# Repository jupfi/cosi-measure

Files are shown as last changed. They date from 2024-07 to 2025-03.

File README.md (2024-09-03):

# COSI Measure

COSI Measure

<!-- TOC -->

- [COSI Measure](#cosi-measure)
  - [Description](#description)
  - [System specifications](#system-specifications)
  - [Versions and Branches](#versions-and-branches)
  - [Contacts](#contacts)
    - [Known builds](#known-builds)
  - [Contributors alphabetical order](#contributors-alphabetical-order)
  - [Publications](#publications)
  - [Acknowledgments](#acknowledgments)
  - [License and Liability](#license-and-liability)

<!-- /TOC -->
## Description

COSI Measure is an open source multipurpose 3-axis robot operating in a large volume, that can be equipped with e.g. field mapping probes for static or dynamic field measurements (electromagnetic, temperature etc.). Submillimeter fidelity and reproducibility/backlash performance were evaluated experimentally. It can be potentially upgraded to be used as a CNC, for 3D printing or other applications, that require reproducible submillimeter movements.

## System specifications

- Dimension: (80x90x105)cm³
- Working volume: (53x53x64)cm³
- Precision: positioning error <1mm
- Max load: ~20kg
- Applied force: 896N (91kg)
- Standalone system
- Inductive limit switches
- Emergency Stop
- Open Source Software GUI (Python)
- Estimated material costs: ~2000€

More photos and videos can be found on opensourceimaging.org: <https://www.opensourceimaging.org/project/cosi-measure/>

## Versions and Branches

You're currently viewing the `main` branch, showing ongoing development on `v2.0.*` of the COSI Measure system.\
New versions are developed in dedicated feature branches and then merged here.

The latest stable release is [v2.0](https://github.com/opensourceimaging/cosi-measure/releases/tag/v2.0).

For older, please check out the [releases overview](https://github.com/opensourceimaging/cosi-measure/releases/).

The changes between versions are summarized in the respective release notes and documented in the [CHANGELOG](CHANGELOG.md) document.

## Contacts

General contact:
Name | Email | Institution | COSI Measure Applications
-----|-----|-----|-----|
Lukas Winter | <lukas.winter@ptb.de> | Physikalisch-Technische Bundesanstalt (PTB), Berlin, Germany | Magnetic field mapping of MR magnets, implant safety measurements, RF field mapping of RF coils using time-domain H- and E-field sensors, Measurements within an MR scanner, 3D printing

COSI Measure Builds

### (Known) builds

Name | Email | Institution | COSI Measure Applications
-----|-----|-----|-----|
Haopeng Han | <haopeng.han@mdc-berlin.de> | Max-Delbrück Center for Molecular Medicine, Berlin, Germany | Temperature and RF field mapping of RF coils
Tom O'Reilly | <t.o_reilly@lumc.nl> | Leiden University Medical Center (LUMC), Leiden, Netherlands | Magnetic field mapping of low field MR magnets
Benjamin Menküc | <benjamin.menkuec@fh-dortmund.de> | University of Applied Sciences, Dortmund, Germany | Magnetic field mapping of low field MR magnets
Mark Bason | <M.Bason@sussex.ac.uk> | Quantum Systems and Devices, University of Sussex, Falmer, England | Magnetic field measurements
Wolfgang Kilian | <Wolfgang.Kilian@ptb.de> | Physikalisch-Technische Bundesanstalt (PTB), Berlin, Germany | 3D printing of phantoms

## Contributors (alphabetical order)

Nils Allek, Mark Bason, Jan Gregor Frintz, Haopeng Han, Amjad Kasabashy, Wolfgang Kilian, Ilia Kulikov, Benjamin Menküc, Tobias Mohr, Reiner Montag, Tom O'Reilly, David Shiers, Berk Silemek, Karl Stupic, Lukas Winter

## Publications

If you find this useful in your work, please cite:
[H. Han, R. Moritz, E. Oberacker, H. Waiczies, T. Niendorf and L. Winter, "Open Source 3D Multipurpose Measurement System with Submillimetre Fidelity and First Application in Magnetic Resonance", Scientific Reports, 7:13452, 2017](https://nature.com/articles/s41598-017-13824-z)

## Acknowledgments

This work is supported by the Open Source Imaging Initiative (OSI²), <https://www.opensourceimaging.org/project/cosi-measure/>

The project (21NRM05) has received funding from the European Partnership on Metrology, co-financed by the European Union's Horizon Europe Research and Innovation Programme and by the Participating States.

## License and Liability

The content in this repository is licensed under the CERN Open Hardware Licence Version 2 - Weakly Reciprocal, please see [LICENSE](LICENSE) for details and also check the [DISCLAIMER](DISCLAIMER.pdf)

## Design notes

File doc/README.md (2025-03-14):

# COSI Measure Assembly

To build your own COSI measure, you will need to complete the following steps:

- Finish the [Mechanical Assembly](mechanical_assembly.md). This contains the steps to assemble the mechanical components of the COSI measure.
- Finish the [Enclosure Assembly](enclosure_assembly.md). This contains the steps for wiring the electronics and assembling the enclosure. This has some subitems that need to be completed in order to finish the enclosure assembly.
  - Build the [Driver Breakoutboard](rumba32/driver_breakoutboard_assembly.md). This contains the steps to assemble the driver breakoutboard.
  - Build the [Endstop Levelshifter](rumba32/endstop_levelshifter_assembly.md). This contains the steps to assemble the endstop levelshifter.
- Finish the wiring of the [Sensors and Actuators](wiring_sensor_actuators.md). This contains the steps for wiring the sensors and actuators to the electronics cabinet.

You can then commission the COSI measure by following the steps in the [Commissioning](comissioning.md) section.

Once you have completed these steps, you will have a fully assembled COSI measure. You can then follow the steps in the [Software Setup](software_setup.md) to configure the software for your COSI measure.

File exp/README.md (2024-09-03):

# Exports

This folder contains all exports that are relevant for the COSI Measure (3D printable STLS, Gerber files, etc.).

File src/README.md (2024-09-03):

# System

Here you can find all necessary files to reproduce the COSI Measure setup.

Please read the [assembly documentation](../doc/README.md) first, in particular you will find some known issues or useful ideas in the comments section, which will help you reproducing the design.

## Mechanical

The mechanical design contains the BoM and technical drawings of the mechanical parts.

## Enclosure

The enclosure design contains the BoM and design files of electronic cabinet components.

## Motors and Sensors

Contains designs for the motors and sensors.

## Software

The software design contains the configuration files for the Klipper firmware.

## Accessories

Contains designs for accessories like the field mapping probe.

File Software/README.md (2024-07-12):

# Software Getting Started

<!-- TOC -->

- [Software Getting Started](#software-getting-started)
    - [Installation](#installation)
        - [Download and Install Klipper](#download-and-install-klipper)
        - [Setting things up!](#setting-things-up)
        - [Config File](#config-file)
        - [Going into Bootloader Mode](#going-into-bootloader-mode)
        - [Flashing MCU and getting new Serial Port](#flashing-mcu-and-getting-new-serial-port)
    - [GUI](#gui)
    - [Commandline Interface](#commandline-interface)

<!-- /TOC -->

COSY Measure is using the open source 3D-printer firmware [klipper](https://www.klipper3d.org/). This document leads you through the installation. It´s assumed you have already installed [Raspberry-Pi-OS](https://www.raspberrypi.com/software/). We recommend the latest 64-bit Desktop version.

## Installation 

This Quick-Start-Guide is a short summary of https://www.klipper3d.org/Installation.html with some modifications for Rumba32 boards.

### 1. Download and Install Klipper

     git clone https://github.com/Klipper3d/klipper
     ./klipper/scripts/install-octopi.sh

Go to [backend/flash_mcu.sh](backend/flash_mcu.sh) and change the path in line 19 to the path of the repository above. For me line 19 is 

     19:  cd /home/cosi/klipper

### 2.1 Setting things up!

     cd klipper
     make menuconfig 

Opens a menu. Set
- Enable extra low-level configuration options
- Micro-controller Architecture (STMicroelectronics STM32)
- Processor model (STM32F446)
- Bootloader offset (32KiB bootloader)
- Clock Reference (12 MHz crystal)
- Communication interface (USB (on PA11/PA12))
- USB ids (doesnt matter. But choose something)
- no GPIO pins to set at startup ()

### 2.2 Config File

Get or write a ```printer.cfg```-file, here is mine: [backend/printer.cfg](backend/printer.cfg)

Save it as a file named "printer.cfg" in the home directory of the pi user (i.e. ```/home/cosi/printer.cfg```).

This file contains all machine configurations. Further reading: https://www.klipper3d.org/Installation.html#obtain-a-klipper-configuration-file

### 3. Going into Bootloader Mode

If not already done, install ```pigpio```for controlling the GPIO pins via the comand line: 

     sudo apt-get install pigpio
     sudo systemctl enable pigpiod
     sudo systemctl start pigpiod

The shell script ```backend/flash_mcu.sh``` will set the Rumba board into bootloader mode and eventually will try to flash the MCU. Execute 

     ./backend/flash_mcu.sh

to set the board into bootloader mode. Because it doesn´t know yet the usb-id of the microcontroller it will fail to flash - ignore that for now. Search the Device ID by executing 

     lsusb

This will show up something like

     Bus 002 Device 001: ID 1d6b:0003 Linux Foundation 3.0 root hub
     Bus 001 Device 031: ID 0483:df11 STMicroelectronics STM Device in DFU Mode
     Bus 001 Device 002: ID 2109:3431 VIA Labs, Inc. Hub

So in my installatiom ```0483:df11``` is the ID of the STM-chip of Rumba32. Change line 20 in ```backend/flash_mcu.sh``` to your device ID and save the file.

### 4. Flashing MCU and getting new Serial Port

Execute ```backend/flash_mcu.sh``` again. Now it shall flash the MCU. This will eventually look something like

     Downloading to address = 0x08008000, size = 29236
     Download	[=========================] 100%        29236 bytes
     Download done.
     File downloaded successfully
     Transitioning to dfuMANIFEST state
     dfu-util: can't detach
     Resetting USB to switch back to runtime mode
     cosi@raspberrypi:~/klipper $ 

Then search for serial ports by executing 

     ls /dev/serial/by-id/*

this will return something similar to 

     /dev/serial/by-id/usb-Klipper_stm32f446xx_280058000951363131343032-if00

Copy and paste it in ```/home/cosi/printer.cfg``` to your MCU serial definition:

     [mcu]
     serial: /dev/serial/by-id/usb-Klipper_stm32f446xx_280058000951363131343032-if00

Congratulations, now you´re done. Get a coffee. Enjoy.

## GUI

A GUI was developed in Python for COSI measure. You can install all required packages (ideally in a virtual environment) by running:

```bash
pip install -r requirements.txt
```

To start the GUI, run:

```bash
python main.py
```

## Commandline Interface

Start the klipper service with executing

     sudo service klipper start

Klipper can be controlled via the following virtual serial port:

     /tmp/printer

Use 250000 Baud for communication. You can send G-code to this serial port and receive status information of the machine, refer to https://www.klipper3d.org/G-Codes.html. 

There are some custom g-code macros for disabling and enabling the drives without letting klipper loose it´s homing, for details see [printer.cfg](backend/printer.cfg) and [driver breakoutboard](../electronic-cabinet/Rumba32/Driver_BreakoutBoard/README.md). Use this commands only at standstill and never run a movement with disabled drives as this would eventually lead to false positioning.

Stop the klipper service by executing

     sudo service klipper stop

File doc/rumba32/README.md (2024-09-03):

# Rumba32

The [Rumba32](https://github.com/Aus3D/RUMBA32) is a 3D-printer mainboard with a microcontroller which is controlling the stepper motors, endstops etc.

- It is not compatible with industrial 12 V or 24 V limit switches so a levelshifter is needed, see [here](endstop_levelshifter_assembly.md).
- It is not designed for external motor drivers with extended safe-torque-off (emergency stop) functionality, so breakoutboards instead of the motor drivers are needed, see [here](driver_breakoutboard_assembly.md).
- The external motor drivers need 5 V signals, thus a little work on the Rumba32 PCB is needed, see [here](driver_breakoutboard_assembly.md#stepper_driver_logic-jumper)
- [Klipper](https://github.com/Klipper3d/klipper) requires a temperature signal from the nozzle and the heated bed. COSI Measure usually does not have this, so please plug two 100 k resistors to the PT100 inputs.

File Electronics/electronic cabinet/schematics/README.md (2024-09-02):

# Schematics and Terminal Plans

<!-- TOC -->

- [Schematics](#schematics)
  - [Power Distribution](#power-distribution)
  - [EmergencyStop](#emergencystop)
    - [Required Specs](#required-specs)
  - [Rumba32 and Motors](#rumba32-and-motors)
    - [NEMA color codes](#nema-color-codes)
  - [RaspberryPi](#raspberrypi)
- [Terminal Plans](#terminal-plans)
  - [X0](#x0)
  - [X1](#x1)
  - [X2](#x2)
  - [X3](#x3)
  - [X4](#x4)
  - [X5](#x5)
  - [X6](#x6)
  - [X7](#x7)
  - [X8](#x8)

<!-- /TOC -->

## Schematics

### Power Distribution

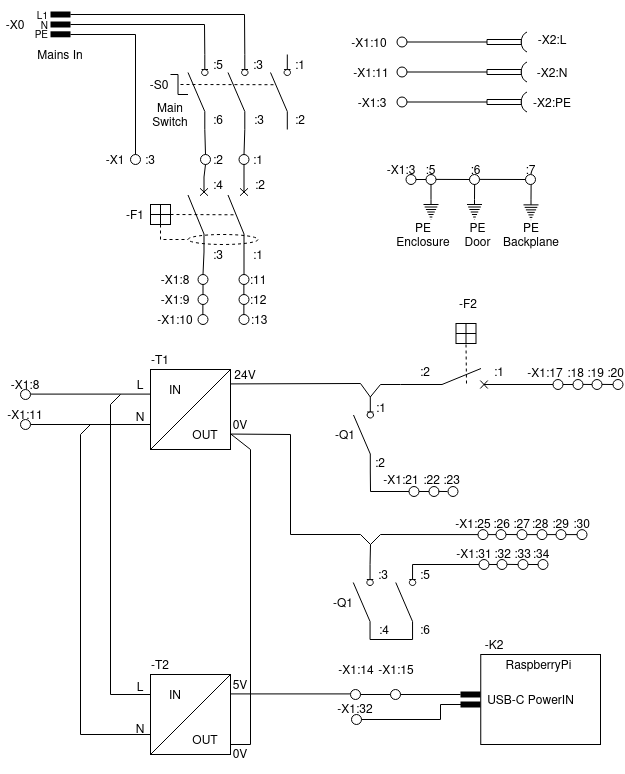
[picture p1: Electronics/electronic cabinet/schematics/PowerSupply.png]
Power Supply Schematic


The contactor $-Q1$ disconnects the motor drivers from the power supply in case of safe-torque-off (aka emergency stop). Schneider Electric has defined this way of wiring in an [application note](https://ckm-content.se.com/ckmContent/sfc/servlet.shepherd/document/download/0691H000008h5vrQAA).

$-F1$ is an overcurrent protection with RCD. Depending to the electric installation of your lab and applicable regional laws it might be optional.

$-F2$ is an overcurrent protection.

### EmergencyStop

It is advisable (and most likely legal obligatory) having a safe-torque-off functionality according to EN-IS0 60204-1 so that the machine can be stopped in case of an emergency. <br>

### Required Specs

- Since the Rumba32 has no failsafe features (SIL-2 or above), the safe-torque-off must be implemented in dedicated hardware.
- To prevent unintended re-start of the drives, a dedicated safety-relais is used (-K1, _XPSUDN13AP_, Schneider Electric). The safety-relais is used with application function '6'. Start function is '1'.
- since there are no stepper motor drivers available with suitable enable inputs (high-active and approved to EN-ISO 60204-1), their enable-inputs can not be used for a safe-torque-off function. So a suitable contactor (DC-3 operation for $20 \ A$ at $24 \ V_{DC}$) must be used to cut-off the power supply to the motor drivers in case of an emergency. This contactor must be selected carefully and wired according to the manufacturers guidelines to ensure safe operation.
- with some bad luck a cheap stepper motor driver can get killed by disrupting the power supply during operation due to the back-EMF of the motor. So a motor driver has to be disabled by the enable pin before interrupting the power supply connection. A 5V signal is sent to the enbable pin of the breakout board if the safety relays turns of. This signal is assumed to be faster than the motors turning off because Q1 is a mechanical relay (switching off the machine by -S0 is always safe: the big $24 \ V$ power supply will slowly turn off the power and eventually take up most of the energy that might return from the drives.)
- The enable input of the motor drivers is used for disabling the drives while performing a field-measurement at an already reached location. This functionality is non safety-relevant, thus it can be implemented the easy way.

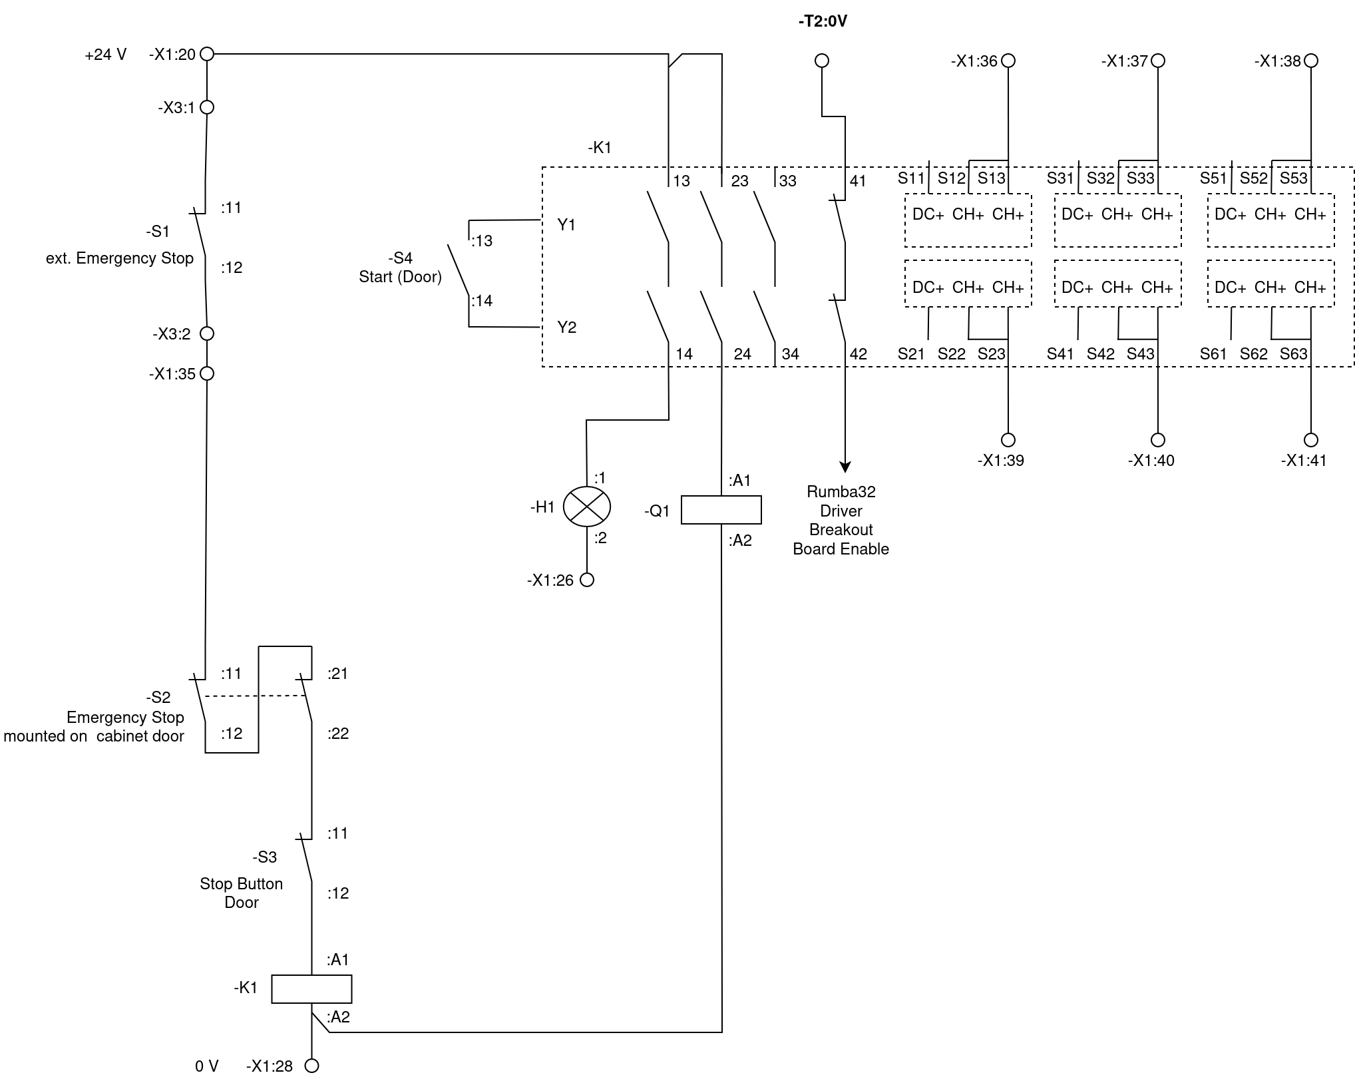
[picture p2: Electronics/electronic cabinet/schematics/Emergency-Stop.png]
Emergency Stop


## Rumba32 and Motors

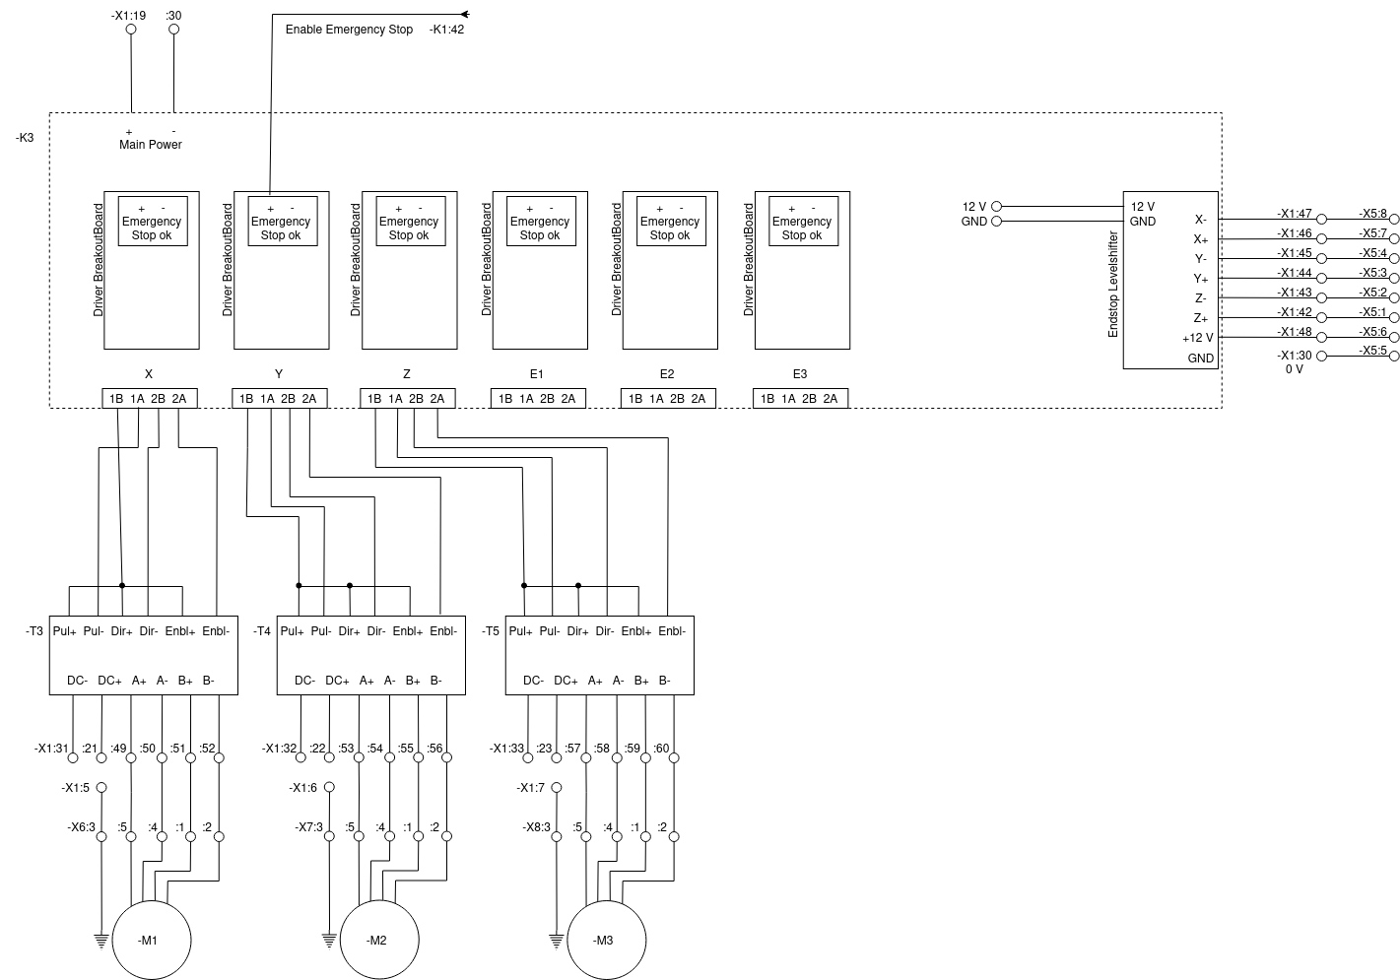
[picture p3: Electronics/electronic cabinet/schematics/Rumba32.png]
Rumba32


The [Rumba32](https://github.com/Aus3D/RUMBA32) is a 3D printer board. It is used for time-critical stuff e.g. generate the step and direction pulses for the stepper motor drivers. <br>
The Driver Breakoutboards are little custom PCBs plugged into the Rumba32, [here](../Rumba32/Driver_BreakoutBoard/README.md) is further documentation about them.

### NEMA color codes

NEMA stepper motors usually have short color-coded wires. Unfortunately, there are multiple colorschemes used. However, some widely used color schemes are in the table below:

| Function  | scheme a  | scheme b  | cable core no | motor connector contact   |
| ----      | ----      | ----      | ----          | ---                       |
| A+        | black     |red        | 1             | :5                        |
| A-        | green     |green      | 2             | :4                        |
| B+        | red       |blue       | 3             | :1                        |
| B-        | blue      |yellow     | 4             | :2                        |
| PE/Shield | -         | -         | gn-yl         | :3                        |

Since the cores of the shielded motor cables are black, they have numbers as identifiers. The $cable \ core \ no$ in the table above is referring to the printed identifier on each core of the cable.

## RaspberryPi

RaspberryPi

## Terminal Plans

## X0

Mains In Connector (IEC-60320 C13/C14)

| Contact   | connected to  |
| ----      | ----          |
| L         | -S0:3         |
| N         | -S0:5         |
| PE        | -X1:3         |

## X1
<!-- New Contacts:

Additional contacts for
- 8 Hardware limit switches
- 2 Software limit switches
- 5V for the motor enable
-->

|Contact #|Comment              |Bridged to contact |Left             |Right  |
|---------|---------------------|-------------------|-----------------|-------|
|1        | L Mains             | -                 | -F1:2           | -S0:3 |
|2        | N Mains             | -                 | -F1:4           | -S0:6 |
|3        | PE                  | PE DIN-rail       | -X1:24          | -X2:PE|
|4        | PE                  | PE DIN-rail       | -T1:PE          | -X0:PE|
|5        | PE                  | PE DIN-rail       | PE Enclosure    | -X6:3 |
|6        | PE                  | PE DIN-rail       | PE Door         | -X7:3 |
|7        | PE                  | PE DIN-rail       | PE Backplane    | -X8:3 |
|8        | L, fused            | 9                 | -T1:L           |       |
|9        | L, fused            | 8 + 10            | -F1:3           |       |
|10       | L, fused            | 9                 |                 | -X2:L |
|11       | N, fused            | 12                | -T1:N           | -X2:N |
|12       | N, fused            | 11 + 13           | -F1:1           |       |
|13       | N, fused            | 12                |                 |       |
|14       | 5 V                 | 15                | -T2:V+          |       |
|15       | 5 V                 | 14 + 16           | -K2:USB-V+      |       |
|16       | 5 V                 | 14                |                 |       |
|17       | 24 V                | 18                | -F2:1           |       |
|18       | 24 V                | 17 + 19           |                 |       |
|19       | 24 V                | 18 + 20           | -K3:+           | -X4:6 |
|20       | 24 V                | 19                | -K1:13          | -X3:1 |
|21       | 24 V switched       | 22                | -T3:DC+         | -Q1:2 |
|22       | 24 V switched       | 21 + 23           | -T4:DC+         | -Q1:2 |
|23       | 24 V switched       | 22                | -T5:DC+         |       |
|24       | 0 V / PE            | 25                | -X1:3           |       |
|25       | 0 V                 | 24 + 26           | -T1:-V          | -X4:5 |
|26       | 0 V                 | 25 + 27           | -H1:2           |       |
|27       | 0 V                 | 26 + 28           | -T2:-           |       |
|28       | 0 V                 | 27 + 29           | -K1:A2          |       |
|29       | 0 V                 | 28 + 30           | -K2:USB-GND     |       |
|30       | 0 V                 | 29                | -K3:-           | -X5:5 |
|31       | 0 V switched        | 32                | -T3: DC-        | -Q1:L3|
|32       | 0 V switched        | 31 + 33           | -T4:DC-         | -Q1:L3|
|33       | 0 V switched        | 32 + 34           | -T5:DC-         |       |
|34       | 0 V switched        |                   | -T6:DC-         |       |
|35       | ext. Emergency-Stop |                   | -S2:11          | -X3:2 |
|36       | Z+(Hardware)        | -                 | -K1:S13         | -X4:1 |
|37       | Z-(Hardware)        | -                 | -K1:S33         | -X4:2 |
|38       | Y+(Hardware)        | -                 | -K1:S53         | -X4:3 |
|39       | Y-(Hardware)        | -                 | -K1:S23         | -X4:4 |
|40       | X+(Hardware)        | -                 | -K1:S43         | -X4:7 |
|41       | X-(Hardware)        | -                 | -K1:S63         | -X4:8 |
|42       | Z+(Software)        | -                 | -K3:Z+          | -X5:1 |
|43       | Z-(Software)        | -                 | -K3:Z-          | -X5:2 |
|44       | Y+(Software)        | -                 | -K3:Y+          | -X5:3 |
|45       | Y-(Software)        | -                 | -K3:Y-          | -X5:4 |
|46       | X+(Software)        | -                 | -K3:X+          | -X5:7 |
|47       | X-(Software)        | -                 | -K3:X-          | -X5:8 |
|48       | 12 V Endstop        |                   | -K3:12V Endstops| -X5:6 |
|49       | -M1:A+              |                   | -T3:A+          | -X6:5 |
|50       | -M1:A-              |                   | -T3:A-          | -X6:4 |
|51       | -M1:B+              |                   | -T3:B+          | -X6:1 |
|52       | -M1:B-              |                   | -T3:B-          | -X6:2 |
|53       | -M2:A+              |                   | -T4:A+          | -X7:5 |
|54       | -M2:A-              |                   | -T4:A-          | -X7:4 |
|55       | -M2:B+              |                   | -T4:B+          | -X7:1 |
|56       | -M2:B-              |                   | -T4:B-          | -X7:2 |
|57       | -M3:A+              |                   | -T5:A+          | -X8:5 |
|58       | -M3:A-              |                   | -T5:A-          | -X8:4 |
|59       | -M3:B+              |                   | -T5:B+          | -X8:1 |
|60       | -M3:B-              |                   | -T5:B-          | -X8:2 |
|61       |                     |                   |                 |       |
|62       |                     |                   |                 |       |
|63       |                     |                   |                 |       |
|64       |                     |                   |                 |       |
|65       |                     |                   |                 |       |
|66       |                     |                   |                 |       |
|67       |                     |                   |                 |       |
|68       |                     |                   |                 |       |
|69       |                     |                   |                 |       |
|70       |                     |                   |                 |       |

The contacts 61 to 70 are reserved for future upgrades, e.g. additional axis.

## X2

External Power Socket

| Contact   | connected to  |
| ----      | ----          |
| L         | -X1:10        |
| N         | -X1:11        |
| PE        | -X1:7         |

## X3

External Emergency Stop Connector

| Contact | Comment     | Connected To |
|---------|-------------|--------------|
| 1       | +24 V       | -X1:19       |
| 2       | Switch Out  | -X1:35       |
| 3       | -           | -            |

## X4

Hardware Endstops Connector 10 pin

| Contact | Comment    | Connected To |
|---------|------------|--------------|
| 1       | Z+         | -X1:35       |
| 2       | Z-         | -X1:36       |
| 3       | Y+         | -X1:38       |
| 4       | Y-         | -X1:39       |
| 5       | 0 V        | -X1:24       |
| 6       | 24V        | -X1:18       |
| 7       | X+         | -X1:40       |
| 8       | X-         | -X1:41       |
| 9       | -          | -            |
| 10      | -          | -            |

## X5

Software Endstops Connector 10 PIN

| Contact | Comment | Connected To |
|---------|---------|--------------|
| 1       | Z+      | -X1:42       |
| 2       | Z-      | -X1:43       |
| 3       | Y+      | -X1:44       |
| 4       | Y-      | -X1:45       |
| 5       | 0V      | -X1:29       |
| 6       | 12 V    | -X1:37       |
| 7       | X+      | -X1:46       |
| 8       | X-      | -X1:47       |
| 9       | -       | -            |
| 10      | -       | -            |

## X6

Motor X-Axis Connector (GX20 5-pin)

| Contact | Comment     | Connected To |
|---------|-------------|--------------|
| 1       | B+          | -X1:50       |
| 2       | B-          | -X1:51       |
| 3       | PE & Shield | -X1:5        |
| 4       | A-          | -X1:49       |
| 5       | A+          | -X1:48       |

## X7

Motor Y-Axis Connector (GX20 Shieled 5-pin)

| Contact | Comment     | Connected To |
|---------|-------------|--------------|
| 1       | B+          | -X1:54       |
| 2       | B-          | -X1:55       |
| 3       | PE & Shield | -X1:6        |
| 4       | A-          | -X1:53       |
| 5       | A+          | -X1:52       |

## X8

Motor Z-Axis Connector (GX20 Shielded 5 pin)

| Contact | Comment     | Connected To |
|---------|-------------|--------------|
| 1       | B+          | -X1:58       |
| 2       | B-          | -X1:59       |
| 3       | PE & Shield | -X1:7        |
| 4       | A-          | -X1:57       |
| 5       | A+          | -X1:56       |

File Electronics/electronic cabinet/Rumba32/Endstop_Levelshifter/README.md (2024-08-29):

# Endstop BreakoutBoard

Breakout Board

This breakoutboard needs to be placed into Rumba32 Endstop connector. It is a levelshifter for the 12 V Endstops.

12V is supplied by Rumba32, you need to connect the 12V Pins of Rumba32 to J4 of this breakout board.

## Schematic

Schematic

## BOM

| ld  | Designator  | Quantity  | Comment            | Manufacturer Part No  | Link Digikey                                                                           |
|---- |------------ |---------- |------------------- |---------------------- |--------------------------------------------------------------------------------------- |
| 1   | J1          | 1         | Screw Terminal     | 691210910008          | <https://www.digikey.de/de/products/detail/w%C3%BCrth-elektronik/691210910008/11478428>  |
| 2   | C1          | 1         | 10n                | C0805C103K2RECAUTO    | <https://www.digikey.de/de/products/detail/kemet/C0805C103K2RECAUTO/8646745>             |
| 3   | J4          | 1         | 2 Pin Header 2.54  | 0022289020            | <https://www.digikey.de/de/products/detail/molex/0022289020/3158803>                     |
| 4   | J3          | 1         | 3 Pin Header 2.54  | 801-87-003-10-001101 | <https://www.digikey.de/de/products/detail/preci-dip/801-87-003-10-001101/3757430>       |
| 5   | J2          | 1         | 5 Pin Header 2.54  | 801-87-005-10-001101  | <https://www.digikey.de/de/products/detail/preci-dip/801-87-005-10-001101/3757433>       |
| 6   | IC1         | 1         | Buffer             | 74HC4050PW,118        | <https://www.digikey.de/de/products/detail/nexperia-usa-inc/74HC4050PW-118/1230398>      |

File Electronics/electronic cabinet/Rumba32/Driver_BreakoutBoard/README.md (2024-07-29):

# Driver Breakout Board

<!-- TOC -->

- [Driver Breakout Board](#driver-breakout-board)
  - [Enable Logic](#enable-logic)
  - [Schematic](#schematic)
  - [BOM](#bom)
  - [Setting jumpers on Rumba32](#setting-jumpers-on-rumba32)
    - [STEPPER_DRIVER_LOGIC JUMPER](#stepper_driver_logic-jumper)
    - [Additional Software Enable Jumpers](#additional-software-enable-jumpers)

<!-- /TOC -->

Breakout Board

This breakoutboard can be placed to the motor driver slots into the Rumba32 board.
It is useful for wiring the step, direction and enable pins via the motor connector to external motor drivers. In addition it supports an easy way of integrating a drive-enable functionality.

## Enable Logic

There can be current on the drives, if

- The Firmware enables the drives and
- some control pins are low (further explanation below) and
- Emergency Stop Relais provides it's NPN-ok signal ($0 \ V$).
- Contactor -Q1 is closed (no safe-torque-off)

Many 3D-printing firmwares are not designed for switching off the drives completely while executing a G-code file. But COSI-Measure is meant to perform magnetic measurements, so it must not disturb the measurements with noisy motor currents while performing a measurement.

A convenient workaround for Klipper is to switch on and off some extra GPIO Pins, that are wired to the hardware-enable-logic. In case you are doing something different and you do not need this feature, feel free to ignore it. Default of these Pins is low, which is also the enabled state. For details about it see the [printer.cfg](../../../software/backend/printer.cfg) file line 275-317. The drives can be enabled and disabled with g-code macros while keeping the homing active.

The NPN-ok-signal from the emergency stop relais can be daisy-chained with standard 2.54 mm jumpers to the next breakout board.

The enable input of the motordriver is not meant for a safe-torque-off function (emergency stop). Safe-torque-off is implemented in hardware (mechanical relais, contactors etc.), see [schematics](../../schematics/README.md#emergencystop).
Anyway, to prevent driver malfunction the driver will be disabled with semiconductor only circuits before the power supply of the driver will be disconnected. The delay is coming from the slower reaction of mechanical contactors and relais, so no dedicated timing module is needed.

## Schematic

Schematic

## BOM

This Bill-of-Materials is for 1 breakout board only. You need one breakout board for each motor with external motor drivers, usually 3 in total (depending to your setup).

| #  | Designator | Quantity | Comment              | Man. Part-No       | Link                                                                                            |
|----|------------|----------|----------------------|--------------------|-------------------------------------------------------------------------------------------------|
| 1  | C1         | 1        | 10 nF, 0805          | C0805C103K2RECAUTO | <https://www.digikey.de/de/products/detail/kemet/C0805C103K2RECAUTO/8646745>                    |
| 2  | D1         | 1        | Dual LED red/green   | AAA3528ESGCT       | <https://www.digikey.de/de/products/detail/kingbright/AAA3528ESGCT/7318936>                     |
| 3  | IC1        | 1        | OR-Gate              | SN74ACT32PWR       | <https://www.digikey.de/en/products/detail/texas-instruments/SN74ACT32PWR/376063>               |
| 4  | J1, J2     | 2        | 8 pin header 2.54    | 61300811121        | <https://www.digikey.de/de/products/detail/w%C3%BCrth-elektronik/61300811121/4846839>           |
| 5  | J3, J5     | 2        | 2 pin header 2.54    | 61300211121        | <https://www.digikey.de/de/products/detail/w%C3%BCrth-elektronik/61300211121/4846823>           |
| 6  | J4         | 1        | 2 pos screw terminal | 0393570002         | <https://www.digikey.de/de/products/detail/molex/0393570002/946543>                             |
| 7  | Q1         | 1        | NPN Transistor       | MMBT3904           | <https://www.digikey.de/de/products/detail/micro-commercial-co/MMBT3904-TP/717280>              |
| 8  | R1         | 1        | 47 kOhm, 0805        | WR08X473 JTL       | <https://www.digikey.de/de/products/detail/walsin-technology-corporation/WR08X473-JTL/13240617> |
| 9  | R2         | 1        | 270 Ohm, 0805        | RMCF0805JT270R     | <https://www.digikey.de/de/products/detail/stackpole-electronics-inc/RMCF0805JT270R/1757887>    |
| 10  | R3, R5    | 2        | 200 Ohm, 0805        | RMCF0805FT200R     | <https://www.digikey.de/de/products/detail/stackpole-electronics-inc/RMCF0805FT200R/1760343>    |
| 11 | R4         | 1        | 1.2 kOhm, 0805       | RMCF0805JT1K20     | <https://www.digikey.de/de/products/detail/stackpole-electronics-inc/RMCF0805JT1K20/1757811>    |
| 12 | -          | 3        | 2.54 mm jumper       | QPC02SXGN-RC       | <https://www.digikey.de/en/products/detail/sullins-connector-solutions/QPC02SXGN-RC/2618262>    |

## Setting jumpers on Rumba32

### STEPPER_DRIVER_LOGIC JUMPER

The STEPPER_DRIVER_LOGIC jumper (see picture below) selects the logic voltage supplied to all stepper driver
sockets. By default, it is configured so that 3.3V is supplied to the stepper drivers. However, since the external motor drivers need 5 V, the track between the centre and 3V pad should be cut, and a solder joint placed over the 5V and centre pad. <br>
voltage selection <br>
(picture and parts of the text above borrowed from <https://github.com/Aus3D/RUMBA32/blob/master/Resources/Manual/RUMBA32%20V1.1%20User%20Manual%20-%20REV%20A.pdf>, License: GPLv2)

### Additional Software Enable Jumpers

Set the jumpers beneath the breakoutboards as seen in the picture below (blue):

jumper placement <br>
(Picture borrowed and modified from <https://github.com/Aus3D/RUMBA32?tab=readme-ov-file>, License: GPLv2)

These jumpers are connecting some GPIO-Pins to the enable logic of this breakout board.

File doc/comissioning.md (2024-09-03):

# Commissioning

This section contains the steps to commission the COSI measure. This includes the steps to ensure that the machine is properly assembled and ready for use.

## 1. Setup

Do the following steps to commission the machine:

1. Connect the machine to the enclosure.
2. Unplug the USB power supply of the RaspberryPi!
3. Ensure/ measure that the PE is correct
4. Connect to mains
5. Ensure and test that all safety related things are working properly, e.g. that the safe-torque-off (emergency stop) is working correct. In case you have hardware limit switches you need them connected for testing.

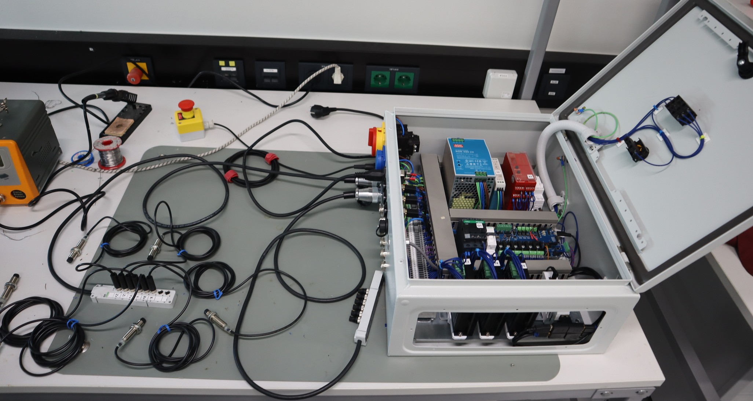
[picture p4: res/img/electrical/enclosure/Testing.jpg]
Testing of Hardware Limit Switches

---
Figure: Testing of the hardware limit switches. As soon as one of the limit switches is triggered the safety relay should turn off.

## 2. Set the DIP-switches of the motor drivers:

For T3:

| Switch # | Comment           | Switch Position |
|----------|-------------------|-----------------|
| SW1      | Current Setting   | ON              |
| SW2      | Current Setting   | ON              |
| SW3      | Current Setting   | OFF             |
| SW4      | Halt Current      | OFF             |
| SW5      | Microstep Setting | ON              |
| SW6      | Microstep Setting | OFF             |
| SW7      | Microstep Setting | OFF             |
| SW8      | Microstep Setting | ON              |

For T4:

| Switch # | Comment           | Switch Position |
|----------|-------------------|-----------------|
| SW1      | Current Setting   | ON              |
| SW2      | Current Setting   | ON              |
| SW3      | Current Setting   | OFF             |
| SW4      | Halt Current      | OFF             |
| SW5      | Microstep Setting | ON              |
| SW6      | Microstep Setting | OFF             |
| SW7      | Microstep Setting | OFF             |
| SW8      | Microstep Setting | ON              |

For T5:

| Switch # | Comment           | Switch Position |
|----------|-------------------|-----------------|
| SW1      | Current Setting   | OFF             |
| SW2      | Current Setting   | OFF             |
| SW3      | Current Setting   | ON              |
| SW4      | Halt Current      | OFF             |
| SW5      | Microstep Setting | ON              |
| SW6      | Microstep Setting | OFF             |
| SW7      | Microstep Setting | OFF             |
| SW8      | Microstep Setting | ON              |

You can later tune the [microstepping](https://www.analog.com/en/lp/001/optimizing-stepper-motors-microstepping.html) and the motor currents to your setup. The table above might be a good starting point. <br>Keep in mind: If you change the microstep settings on the motor drivers, you also need to change it in the [printer.cfg](../src/software/printer.cfg)-file.<br>

A higher microstep setting reduces the holding torque which can be compensated by more current. Having too much microsteps per full step with not enough current leads to less precise movement and increased oscillation. More info on that: <https://www.monolithicpower.com/why-microstepping-isnt-as-good-as-you-think>

## 3. Turn off the main switch

Now wait until the 5V powersupply is discharged and then put back the USB power supply to RaspberryPi. Now you are ready to start with the [software](../Software/README.md).

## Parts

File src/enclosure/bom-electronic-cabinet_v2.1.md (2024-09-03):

# Bill of Materials for the Electronic Cabinet

| Position | Description                       | Designator                | Qty | Manufacturer       | Manufacturer PartNo | Distributor | Comment                                                                                                                              | Link                                                                                                       |
|----------|-----------------------------------|---------------------------|-----|--------------------|---------------------|-------------|--------------------------------------------------------------------------------------------------------------------------------------|------------------------------------------------------------------------------------------------------------|
| 1        | Enclosure                         | -                         | 1   | Schneider Electric | NSYS3D6420P         | reichelt    |                                                                                                                                      | [Link](https://www.reichelt.de/stahlgehaeuse-s3d-mit-montageplatte-600-x-400-x-200-ip66-nsys3d6420p-p310670.html)            |
| 2        | DIN Rails                         | -                         | 2   |                    | 3575ZG-1M           | reichelt    |                                                                                                                                      | [Link](https://www.reichelt.de/at/de/hutschiene-35-x-7-5-mm-gelocht-1-m-hs-35x7-5-1m-p295662.html)                               |
| 3        | Cage Clamp bl                     | X1                        | 5   | WAGO               | 280-904             | reichelt    |                                                                                                                                      | [Link](https://www.reichelt.de/at/de/durchgangsklemme-2-leiter-1-pol-0-08-2-5-mm-wago-280-904-p32237.html)                     |
| 4        | Cage Clamp gn-yl                  | X1                        | 5   | WAGO               | 280-907             | reichelt    |                                                                                                                                      | [Link](https://www.reichelt.de/durchgangsklemme-2-leiter-1-pol-0-08-2-5-mm-wago-280-907-p32238.html)                           |
| 5        | Cage Clamp gy                     | X1                        | 53  | WAGO               | 280-901             | reichelt    |                                                                                                                                      | [Link](https://www.reichelt.de/at/de/durchgangsklemme-2-leiter-1-pol-0-08-2-5-mm-wago-280-901-p32236.html)                     |
| 6        | Terminal Block Endcap             | X1                        | 1   | WAGO               | 280-308             | reichelt    |                                                                                                                                      | [Link](https://www.reichelt.de/at/de/abschluss-und-zwischenplatte-wago-280-308-p248633.html)                                    |
| 7        | Terminal Block Bridges            | X1                        | 20  | WAGO               | 280-402             | farnell     |                                                                                                                                      | [Link](https://de.farnell.com/wago/280-402/querbr-cker-isoliert-grau/dp/1283454?MER=sy-me-pd-mi-acce)                            |
| 8        | Cable Duct 60x25                  | -                         | 1   | arnocanali         | V6K6025             | reichelt    |                                                                                                                                      | [Link](https://www.reichelt.de/verdrahtungskanal-60x25-mm-1000-mm-v6k6025-p338230.html)                                         |
| 9        | Cable Duct 60x40                  | -                         | 1   | arnocanali         | V6K6040             | reichelt    |                                                                                                                                      | [Link](https://www.reichelt.de/verdrahtungskanal-60x40-mm-1000-mm-v6k6040-p275692.html)                                         |
| 11       | Cable Tube                        | -                         | 1   | Rittal             | 2595.000            | Conrad      |                                                                                                                                      | [Link](https://www.conrad.de/de/p/rittal-sz-2595-000-kabelschlauch-polyethylen-o-x-l-16-mm-x-25-m-1-st-1048519.html)            |
| 12       | Cable Tube Holder                 | -                         | 1   | Rittal             | 2593.000            | Conrad      |                                                                                                                                      | [Link](https://www.conrad.de/de/p/rittal-sz-2593-000-kabelschlauchhalter-polyamid-20-st-1048517.html)                           |
| 13       | Stepper Motor Driver              |                           | 3   | ACT                | DM542               | reichelt    |                                                                                                                                      | [Link](https://www.reichelt.de/schrittmotortreiber-fuer-nema-23-18-50-v-act-dm542-p237924.html)                                 |
| 14       | Main Switch                       | S0                        | 1   |                    |                     | reichelt    |                                                                                                                                      | [Link](https://www.reichelt.de/hauptschalter-3-pol-25-a-eaton-041097-p158862.html)                                                |
| 15       | Mains In                          | X0                        | 1   | Deltron            | RID1042H            | rs          |                                                                                                                                      | [Link](https://de.rs-online.com/web/p/iec-filter/7615775)                                                                       |
| 16       | Power Socket                      | X2                        | 1   | Schneider Electric | PKS52B              | Conrad      |                                                                                                                                      | [Link](https://www.conrad.de/de/p/schneider-electric-pks52b-einbau-steckdose-ip54-ik08-blau-2359161.html)                       |
| 17       | USB Through-Connector             | X8, X9, X10             | 3   | CLIFF              | CP30210NMB          | reichelt    |                                                                                                                                      | [Link](https://www.reichelt.de/sg/de/usb-adapter-ft-1-x-usb-3-0-a-buchse-1-x-usb-3-0-b-buchse-cliff-cp30210nmb-p227661.html)    |
| 18       | HDMI Through-Connector            | X11                       | 1   | Delock             | 86963               | reichelt    |                                                                                                                                      | [Link](https://www.reichelt.de/sg/de/hdmi-a-einbaubuchse-mit-verschlusskappe-ip67-delock-86963-p322711.html)                    |
| 19       | RJ45 Through Connector            | X12                       | 1   | TRU Components     | 4016139055312       | Conrad      |                                                                                                                                      | [Link](https://www.conrad.de/de/p/tru-components-rj45-01-rj45-einbaubuchse-1408770-buchse-einbau-stecker-gerade-polzahl-8p8c-silber-1-st-1408770.html) |
| 20       | 3 pin ext. Emergency Stop Connector | X8                      | 1   | binder             | 99-0608-00-03       | Conrad      |                                                                                                                                      | [Link](https://www.conrad.de/de/p/binder-99-0608-00-03-rundstecker-flanschstecker-gesamtpolzahl-3-serie-rundsteckverbinder-678-1-st-738745.html)  |
| 21       | 10 pin Limit Switches Connector     | X4, X5                        | 2   | binder             | -       | Amazon      | Maybe you can find a better supplier and more standard connector (e.g M16). Just make sure it works with the sensor boxes cable diameter. If you don't use Hardware limit switches you only need one.                                                                                                                          | [Link](https://www.amazon.de/gp/product/B0BRCR4DCB/)  |
| 22       | M8 sensor box 8-WAY 3POLE          | -                        | 2   | -             | -       | Conrad      |If you don't use Hardware limit switches you only need one.                                                                                                                          | [Link](https://www.conrad.de/de/p/wago-757-483-000-005-sensor-aktorbox-passiv-m8-verteiler-mit-metallgewinde-1-st-546710.html?refresh=true)  |
| 23       | 5 pin GX20 Motor XYZ-Axes Connector | X6, X7, X8            | 3   | binder             | 99-000-06           | GTech       |                                                                                                                                      | [Link](https://gtech-shop.de/Steckverbinder-GX)                                                                                 |
| 26       | 24 V Power Supply                 | T1                        | 1   | MEANWELL           | NDR-480-24          | reichelt    |                                                                                                                                      | [Link](https://www.reichelt.de/at/de/schaltnetzteil-hutschiene-480-w-24-v-20-a-mw-ndr-480-24-p264962.html)                      |
| 27       | 5 V PowerSupply                   | T2                        | 1   | MEANWELL           | MDR-20-5            | RS          |                                                                                                                                      | [Link](https://de.rs-online.com/web/p/din-schienen-netzteile/0428449)                                                          |
| 28       | Circuitbreaker, RCD               | F1                        | 1   | Schneider Electric | R9D01613            | reichelt    | often not necessary                                                                                                                  | [Link](https://www.reichelt.de/at/de/fi-ls-schalter-resi9-1p-n-13a-b-char-30ma-typ-a-6ka-r9d01613-p292098.html)                  |
| 29       | Contactor DC3                     | Q1                        | 1   | Schneider Electric | LC1D12BD            | reichelt    | [Link](https://ckm-content.se.com/ckmContent/sfc/servlet.shepherd/document/download/0691H000008h5vrQAA)                             | [Link](https://www.reichelt.de/at/de/leistungsschuetz-tesys-d-1-nc-3-1-no-5-5-kw-12-a-lc1d12bd-p211755.html)                    |
| 30       | Safety Relais                     | K1                        | 1   | Schneider Electric | XPSUDN13AP          | RS          | Only use this one if you plan to also use hardware endstops, otherwise you can use one with no PNP monitoring inputs.               | [Link](https://at.rs-online.com/web/p/sicherheitsrelais/2006137)                                                               |
| 32       | Rumba32                           | K3                        | 1   |                    |                     |             | modification needed see [here](../../doc/rumba32/README.md)                                                                                    |                                                                                                            |
| 33       | Endstop BreakoutBoard             | -                         | 1   |                    |                     |             | see [here](../../doc/rumba32/endstop_levelshifter_assembly.md)                                                                                   |                                                                                                            |
| 34       | Driver BreakoutBoard              | -                         | 3   |                    |                     |             | see [here](../../doc/rumba32/driver_breakoutboard_assembly.md)                                                                                   |                                                                                                            |
| 35       | On-Off Switch                     | S4                        | 1   | Eaton              | M22-DDL-GR          | Conrad      |                                                                                                                                      | [Link](https://www.conrad.de/de/p/eaton-216509-m22-ddl-gr-x1-x0-k11-230-w-doppeldrucktaster-1-x-aus-ein-tastend-ip66-1-st-2306911.html)           |
| 36       | Light for S4 (24V)                | H1                        | 1   | Eaton              | 216557              | Conrad      |                                                                                                                                      | [Link](https://www.conrad.de/de/p/eaton-m22-led-w-led-element-weiss-30-v-dc-ac-1-st-700321.html)                                |
| 37       | Emergency Stop                    | S2                        | 1   | Eaton              | 110938              | Conrad      |                                                                                                                                      | [Link](https://www.conrad.de/de/p/eaton-m22-pv-k01-bvp-not-aus-schalter-1-oeffner-ip66-1-st-2132759.html)                        |
| 38       | USB-C Cable                       | -                         | 1   | hama               | 201594              | Conrad      |                                                                                                                                      | [Link](https://www.conrad.de/de/p/hama-usb-ladekabel-usb-2-0-usb-a-stecker-usb-c-stecker-1-00-m-schwarz-00201594-2886437.html)  |
| 39       | USB A-B Cable                     | -                         | 3   | Delock             | 82580               | Conrad      |                                                                                                                                      | [Link](https://www.conrad.de/de/p/delock-usb-kabel-usb-3-2-gen1-usb-3-0-usb-3-1-gen1-usb-a-stecker-usb-b-stecker-1-00-m-blau-vergoldete-steckkontakte-1880889.html)  |
| 40       | HDMI Cable                        | -                         | 1   | Digitus            | AK-330115-010-S     | Conrad      |                                                                                                                                      | [Link](https://www.conrad.de/de/p/digitus-hdmi-anschlusskabel-hdmi-a-stecker-hdmi-micro-d-stecker-1-00-m-schwarz-ak-330115-010-s-vergoldete-steckkontakte-678202.html)  |
| 41       | Micro USB-Cable                   | -                         | 1   | renkforce          | RF-4316220          | Conrad      |                                                                                                                                      | [Link](https://www.conrad.de/de/p/renkforce-usb-kabel-usb-2-0-usb-a-stecker-usb-micro-b-stecker-1-00-m-schwarz-vergoldete-steckkontakte-rf-4316220-1438740.html)   |
| 42       | Jumper Cables                     | -                         | 1   | Joy-IT             | RB-CB-025           | reichelt    |                                                                                                                                      | [Link](https://www.reichelt.com/entwicklerboards-steckbrueckenkabel-25cm-20-kabel-debo-kabelset-p161046.html)                   |
| 43       | M8 Connector for Limit Switches 3 pole | -                     | 12  | Elecbee             | -          | Amazon    | Again, you can probably find a better supplier than amazon. Just make sure the cable diameter works with these connectors. If you have no hardware limit switches you only need half the amount.                                                                                                                                    | [Link](https://https://www.amazon.de/dp/B07S9KT2NP/ref=cm_sw_r_apanp_mUrexl5EeInkk)                   |
| 44       | Circuit Breaker | -                     | F2  | Schneider             | -          |     |    C4/C6 characteristics                                                                                                                      |                    |
| 45       | Limit Switches | -                     | 12  | Omron             | E2B-M12LN08-WP-B2 2M          | Only 6 if you have not hardware limit switches    |   RS     |  [Link](https://de.rs-online.com/web/p/naherungsschalter/8052614)  |
| 46      | Limit Switch Cable | - | 100m | Kabeltronik | 240402500-1 | Conrad |  | [Link](https://www.conrad.de/de/p/kabeltronik-lifyy-steuerleitung-4-x-0-25-mm-schwarz-240402500-1-meterware-323754.html) |
| 47      | Motor Cable | - | 50m | ÖLFLEX | 0026222/50 | Reichelt |  | [Link](https://www.reichelt.com/it/de/shop/produkt/_elflex_fd_classic_810_cy_-_geschirmt_-_50_m_5_x_0_75_mit_pe-165779) |
| 48 | Cable Chain Small | - | - | Igus | E14.2.038 | Igus |  | [Link](https://www.igus.de/product/series-E14) |
| 49 | Cable Chain Large | - | - | DOLD | CK20 | DOLD | You can also use on from Igus. | [Link](https://www.dold-mechatronik.de/Energiekette-CK-20-40mm-breit-626mm-1000mm-19-Glieder-Anschlusselemente) |

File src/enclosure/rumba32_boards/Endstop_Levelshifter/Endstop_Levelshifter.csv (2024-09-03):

Id | Designator | Package | Quantity | Designation | Supplier and ref
1 | J1 | 691210910008 | 1 | Conn_01x08
2 | C1 | C_0805_2012Metric_Pad1.18x1.45mm_HandSolder | 1 | 10n
3 | J4 | PinHeader_1x02_P2.54mm_Horizontal | 1 | Conn_01x02
4 | J3 | PinSocket_1x03_P2.54mm_Vertical | 1 | Conn_01x03
5 | J2 | PinSocket_1x05_P2.54mm_Vertical | 1 | Conn_01x05
6 | IC1 | TSSOP-16_4.4x5mm_P0.65mm | 1 | 74HC4050PW,118

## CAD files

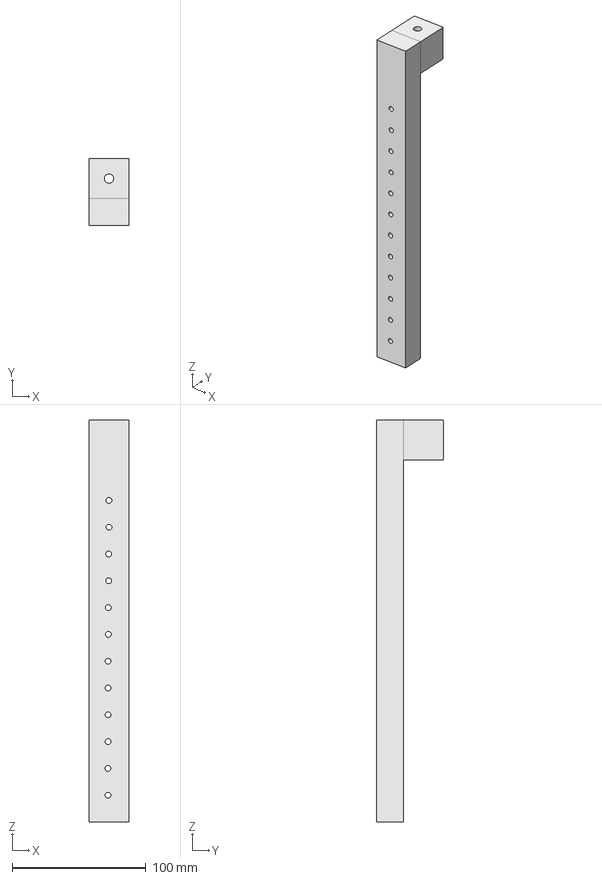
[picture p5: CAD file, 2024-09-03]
src/accessories/Lakeshore 460 Gaussmeter probe holder/Holder_Lakeshore_3-axis_withRod.step
30.0 x 50.0 x 300.0 mm

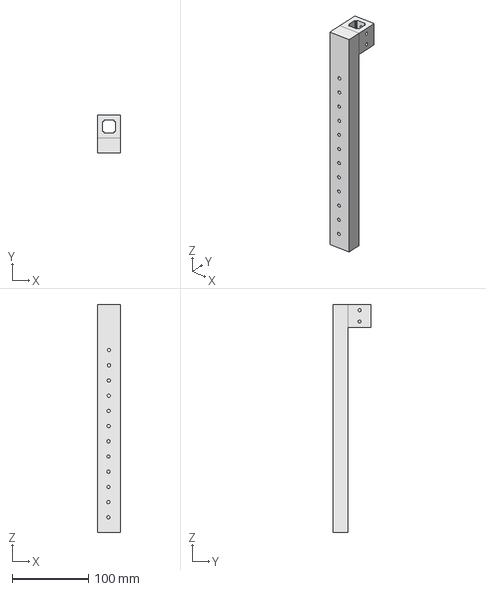
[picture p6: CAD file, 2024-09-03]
src/accessories/Metrolabs PT2026 probe holder/Holder_NMR_Probe_withRod.step
30.0 x 50.0 x 300.0 mm

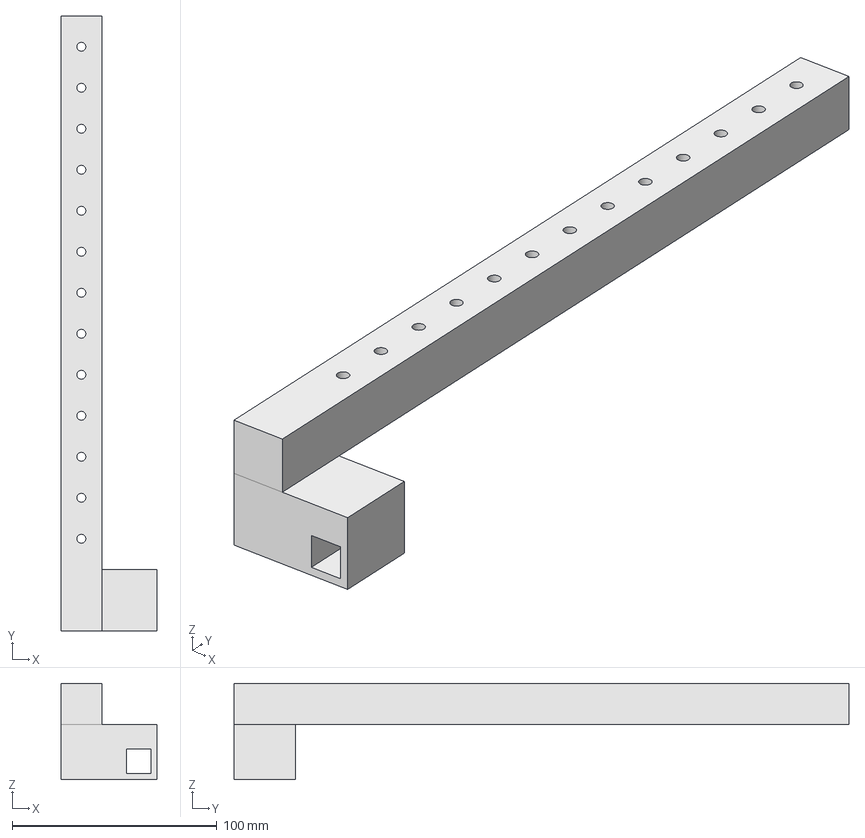
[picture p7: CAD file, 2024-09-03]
src/accessories/SPEAG H1TDS probe holder/H-field_holder_withRod.step
47.0 x 300.0 x 47.0 mm

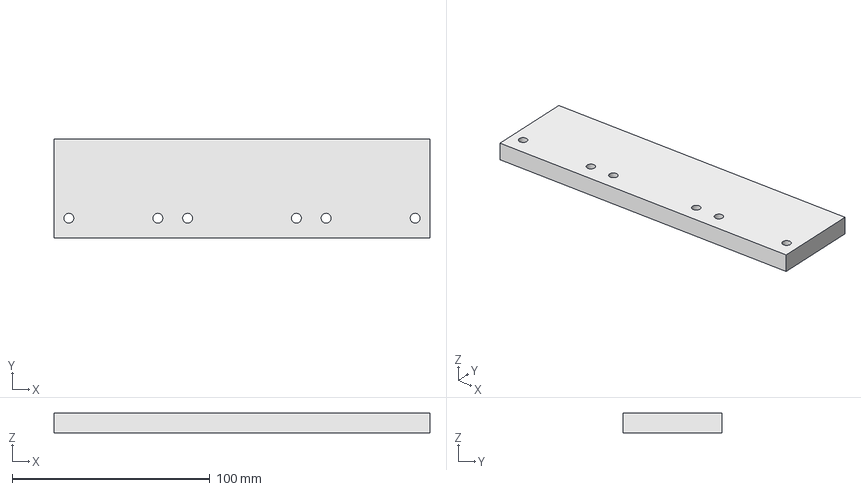
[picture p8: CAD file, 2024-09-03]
src/mechanical/Aluplates/FreeCAD/plate8.FCStd
190.0 x 50.0 x 10.0 mm

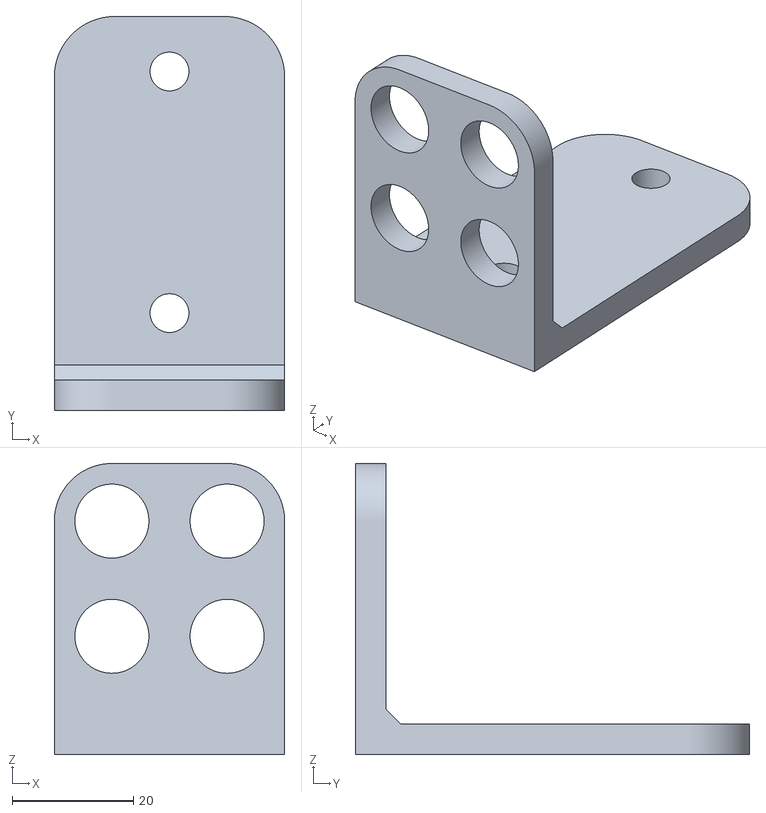
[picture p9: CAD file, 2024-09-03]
src/mechanical/Limit Switch Holder/Sensor Winkel1_kurz.stl
38.0 x 65.0 x 48.0

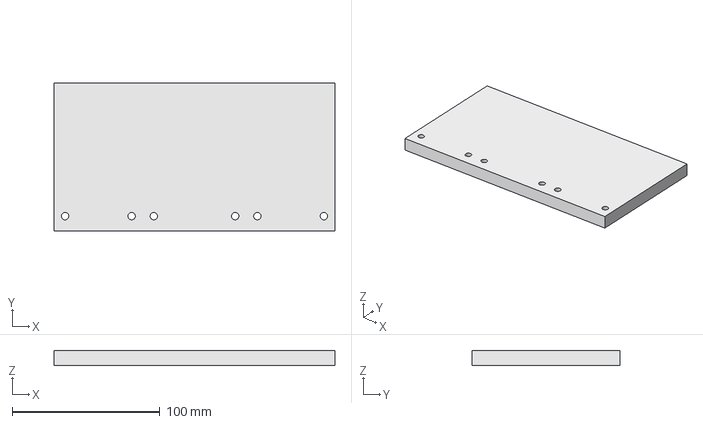
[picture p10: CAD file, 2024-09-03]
src/mechanical/Aluplates/FreeCAD/plate9.FCStd
190.0 x 100.0 x 10.0 mm

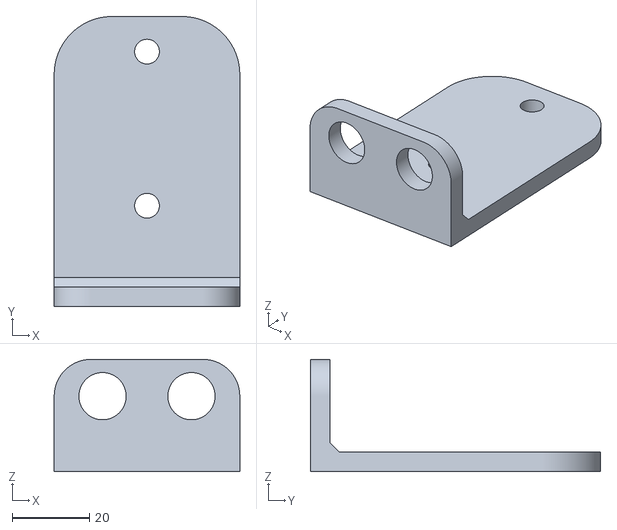
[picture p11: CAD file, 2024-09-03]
src/mechanical/Limit Switch Holder/Sensor Winkel1_kurz_lang.stl
48.0 x 75.0 x 29.0

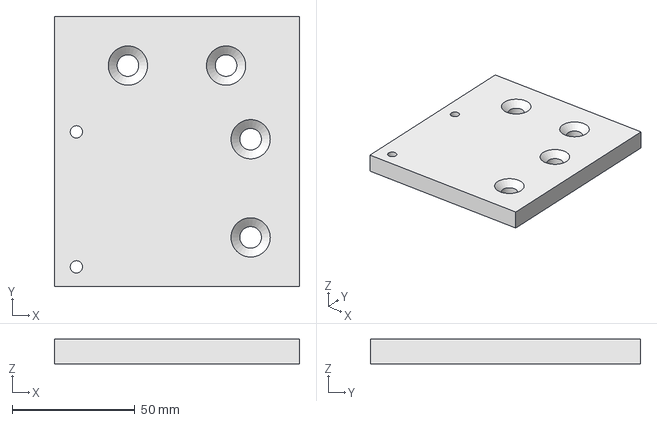
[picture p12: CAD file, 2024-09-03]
src/mechanical/Aluplates/FreeCAD/plate3.FCStd
100.0 x 110.0 x 10.0 mm

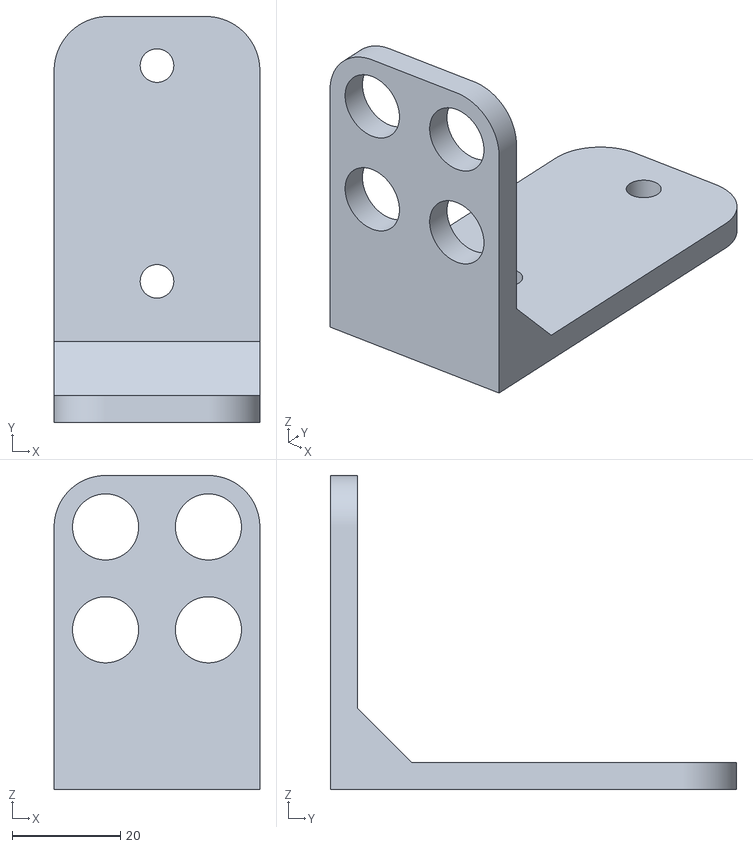
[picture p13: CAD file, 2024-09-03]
src/mechanical/Limit Switch Holder/Sensor Winkel1.stl
38.0 x 75.0 x 58.0

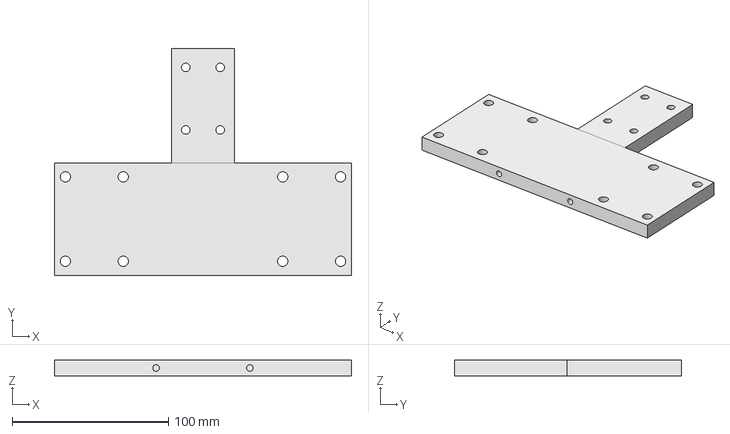
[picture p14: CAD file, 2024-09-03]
src/mechanical/Aluplates/FreeCAD/plate5.FCStd
190.0 x 145.0 x 10.0 mm

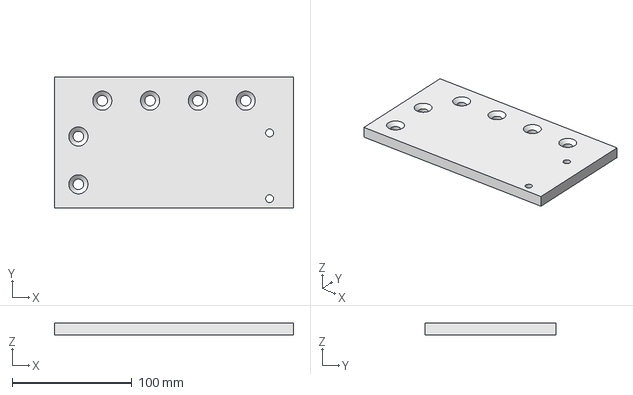
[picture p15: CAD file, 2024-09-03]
src/mechanical/Aluplates/FreeCAD/plate4.FCStd
200.0 x 110.0 x 10.0 mm

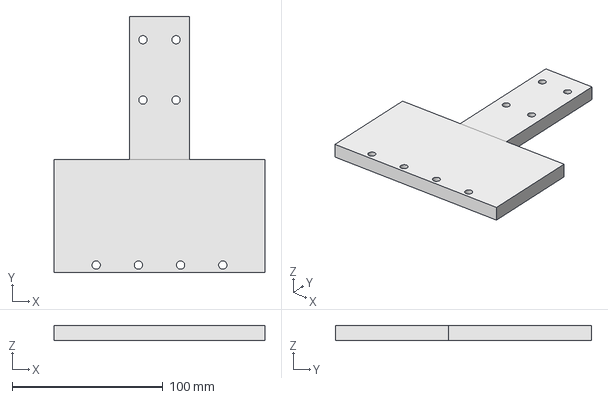
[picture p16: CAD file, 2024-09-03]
src/mechanical/Aluplates/FreeCAD/plate2.FCStd
140.0 x 170.0 x 10.0 mm

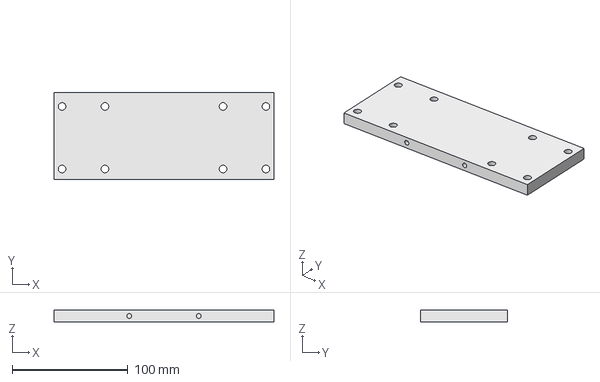
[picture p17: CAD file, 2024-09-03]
src/mechanical/Aluplates/FreeCAD/plate7.FCStd
190.0 x 75.0 x 10.0 mm

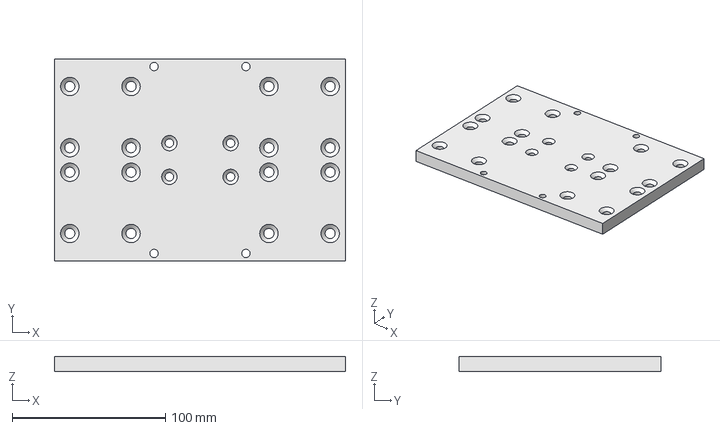
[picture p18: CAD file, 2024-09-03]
src/mechanical/Aluplates/FreeCAD/plate6.FCStd
190.0 x 132.0 x 10.0 mm

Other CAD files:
src/accessories/Lakeshore 460 Gaussmeter probe holder/Holder_Lakeshore_3-axis_withRod_2.stl
src/accessories/SPEAG H1TDS probe holder/H-field_holder_withRod_2.stl
src/mechanical/Aluplates/FreeCAD/plate1.FCStd
src/accessories/Lakeshore 460 Gaussmeter probe holder/Holder_Lakeshore_3-axis_withRod.FCStd
src/accessories/Metrolabs PT2026 probe holder/Holder_NMR_Probe_withRod.FCStd
src/accessories/SPEAG H1TDS probe holder/H-field_holder_withRod.FCStd

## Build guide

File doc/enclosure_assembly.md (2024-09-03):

# COSI Measure Electronic Controls

In this folder are all the files you need to rebuild the electronic cabinet of COSI Measure. In every subfolder is a README.md as a landing page with detailed information on every subsystem.

## Building Instructions

### 1. Buy all needed components

Buy all needed components - see [bom-electronic-cabinet._v2.1.md](../src/enclosure/bom-electronic-cabinet_v2.1.md).

Keep in mind that there are some things missing that most of the labs have laying around e.g. screws, cables...

### 2. Machine all holes in the enclosure

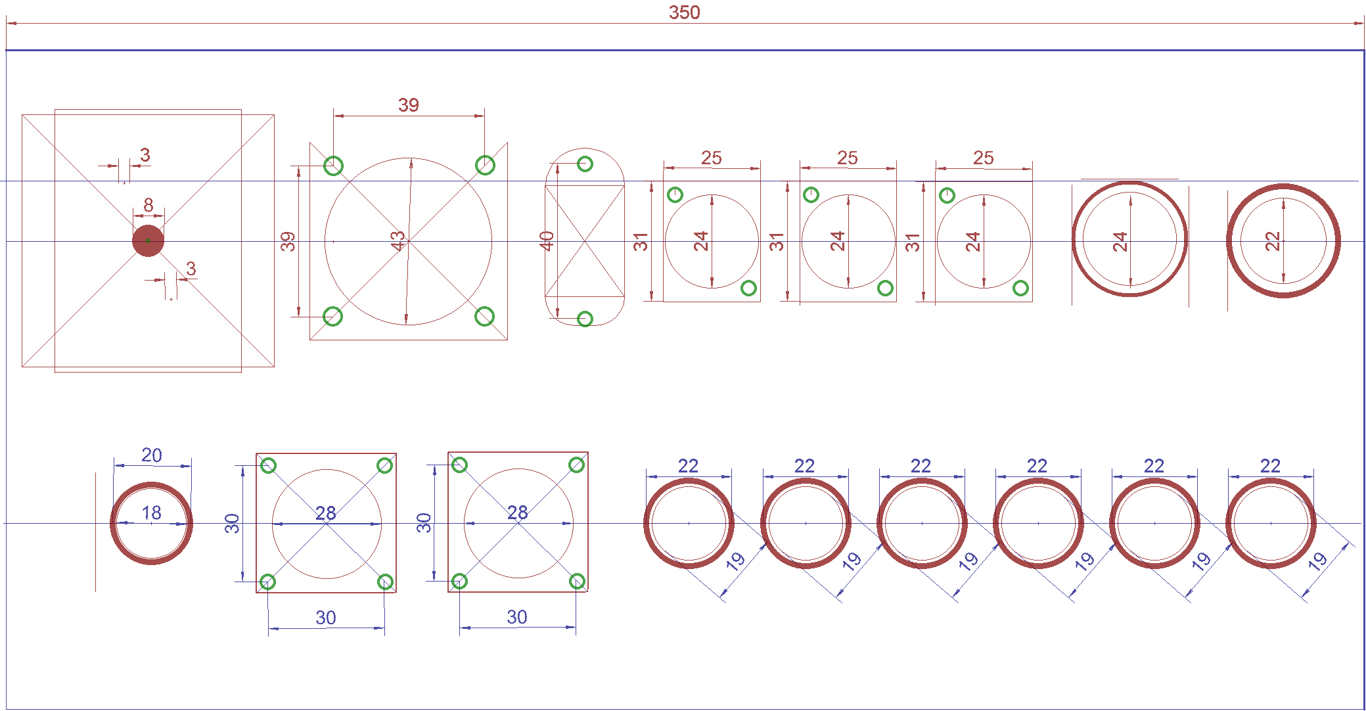
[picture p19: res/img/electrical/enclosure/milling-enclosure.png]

This setup is for all 6 stepper motor drivers and hardware limit switches.

- If you only use 3 drivers, you can omit three of the lower 22mm holes (GX20).
- The lower 28mm holes are for the limit switch connectors. If you don't have hardware limit switches you only need one of those.
- The 8mm hole is for the main switch.
- The 43mm hole is for the 230V outlet.
- To the right of the 43mm hole is the IEC 6032 connector.
- The three 24mm holes are for USB.
- The 24mm to the right of the three USB connectors is HDMI.
- The 22mm to the far right is for the Ethernet connector.

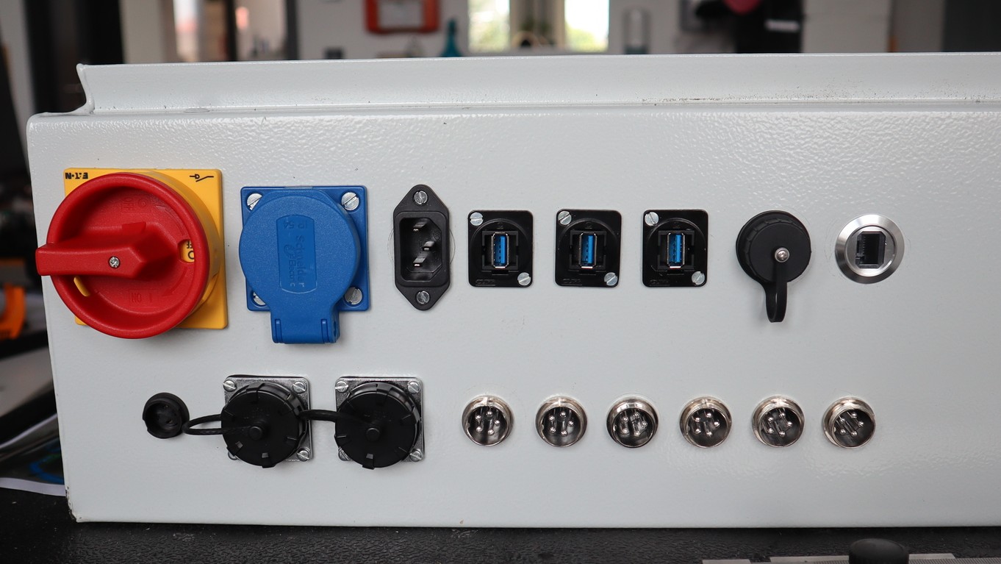
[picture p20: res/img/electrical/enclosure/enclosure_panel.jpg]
Picture of the different connectors


Now drill all of the holes in the door for the:

- Emergency stop button
- ON/OFF switch

<!-- Ok this section has the following changes:

1. Everything is now mounted on DIN rails so I need to add the according 3d printed parts

-->

### 3. Mount all devices to the baseplate and the door

We riveted all of the DIN rails to the baseplate.

⚠️**Important**⚠️ Mount the cable tubing the other way around compared to the picture. This way it's not pulled down by gravity.

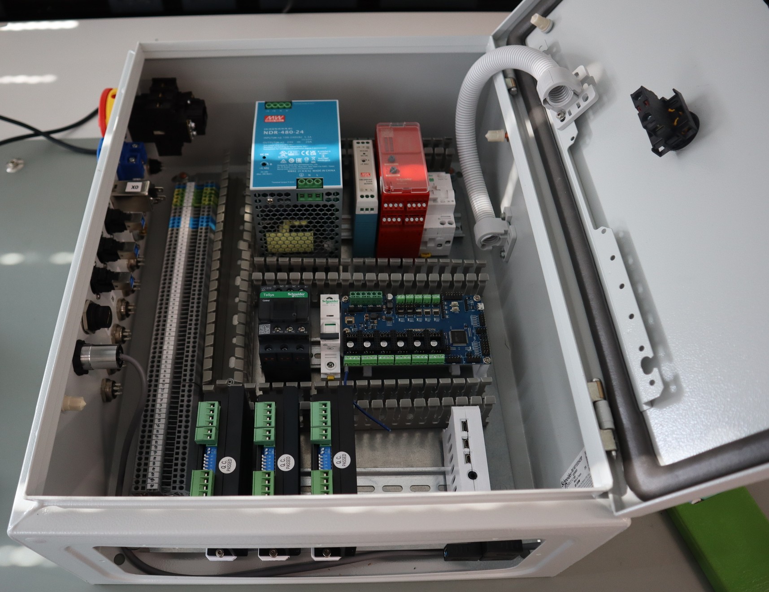
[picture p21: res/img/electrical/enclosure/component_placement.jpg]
Component Placement


The following components are mounted on 3D printed adapters for DIN rails:

- Rumba32 - the STL can be found [here](...) and the clips, which you need to print twice, [here](https://github.com/VoronDesign/Voron-0/blob/d8425f9a4c25db30f294dca77d6cb5cbd6e59c82/STLs/Electronics/PCB_DIN_Clip_x2.stl). You need to assemble the Rumba32 DIN rail mount but it's probably a good idea to first perform the modifications on the Rumba board described in the [Rumba32](rumba32/README.md) section.

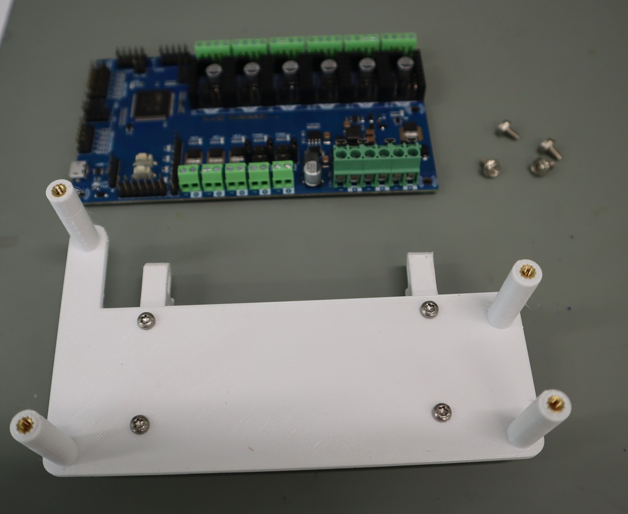
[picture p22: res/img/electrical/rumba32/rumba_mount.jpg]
DIN Rail Mount for Rumba32


- Raspberry Pi - the STL can be found on [thingiverse](https://www.thingiverse.com/thing:3849108).

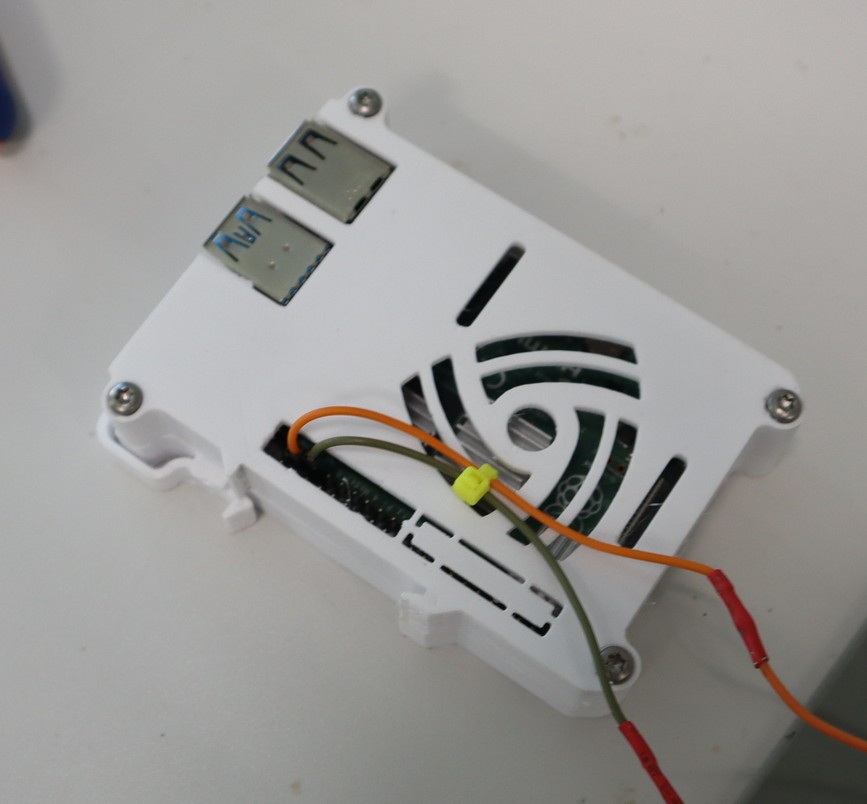
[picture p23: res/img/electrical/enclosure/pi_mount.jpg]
DIN Rail Mount for Raspberry Pi

Figure: DIN rail mount for Raspberry Pi. There are some cables already added to the GPIOs which are connected to the Rumba32. Look at the schematics for more details.

- DMT542 stepper motor drivers - find the STL files on [printables](https://www.printables.com/model/323993-din-rail-dm542-dm556-cnc-stepper-driver-mount-with)

Play around with the scaling a little bit when printing in order to achieve a good fit.

Note: In case you ordered the enclosure from the BoM you probably have more space compared to the picture. Just enjoy the extra space, it makes wiring easier.

### 4. Build the [breakoutboards](rumba32/README.md)

For this see [Levelshifter](rumba32/endstop_levelshifter_assembly.md) and [Driver Breakoutboards](rumba32/driver_breakoutboard_assembly.md). Place them into the Rumba32 board.

### 5. Mount all devices to the door and the side of the enclosure

Add cables to the connectors before hand. This makes it easier to connect everything later on.

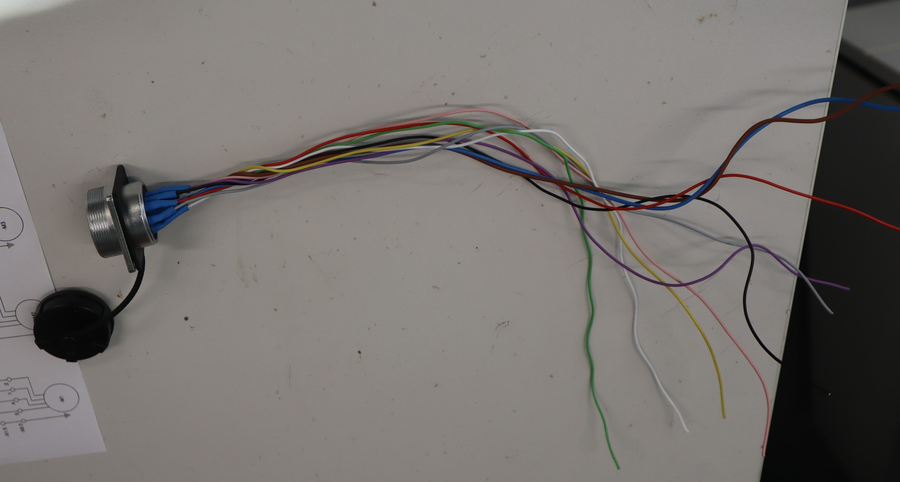
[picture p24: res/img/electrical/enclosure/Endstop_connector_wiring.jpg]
Endstop connector with wires

---

Figure: Endstop connector with wires added. You might have another connector for the endstops, but the principle is the same. If you have hardware endstops you need to do this twice.

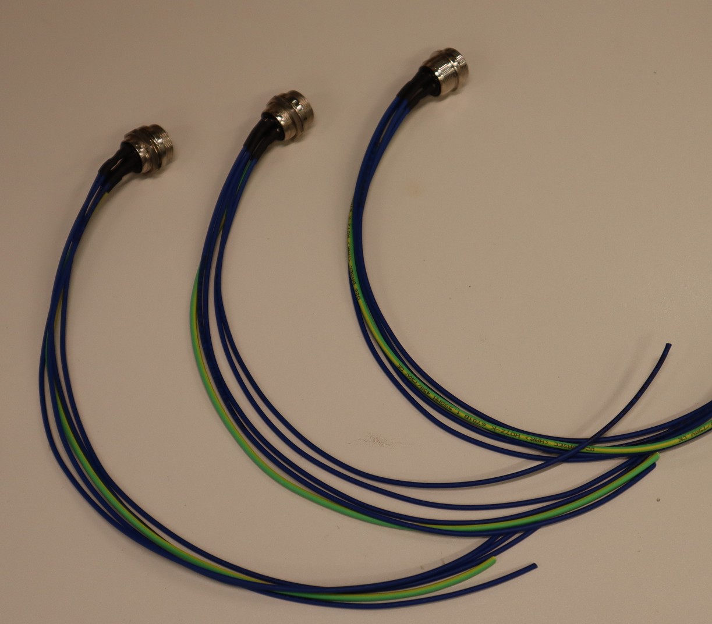
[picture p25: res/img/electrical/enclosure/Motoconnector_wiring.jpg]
Motor connector with wires

---

Figure: Motor connectors with added wires.

### 6. Wire PE, see [schematics](../res/picto/enclosure_schematics/)

Use green-yellow wire for that.

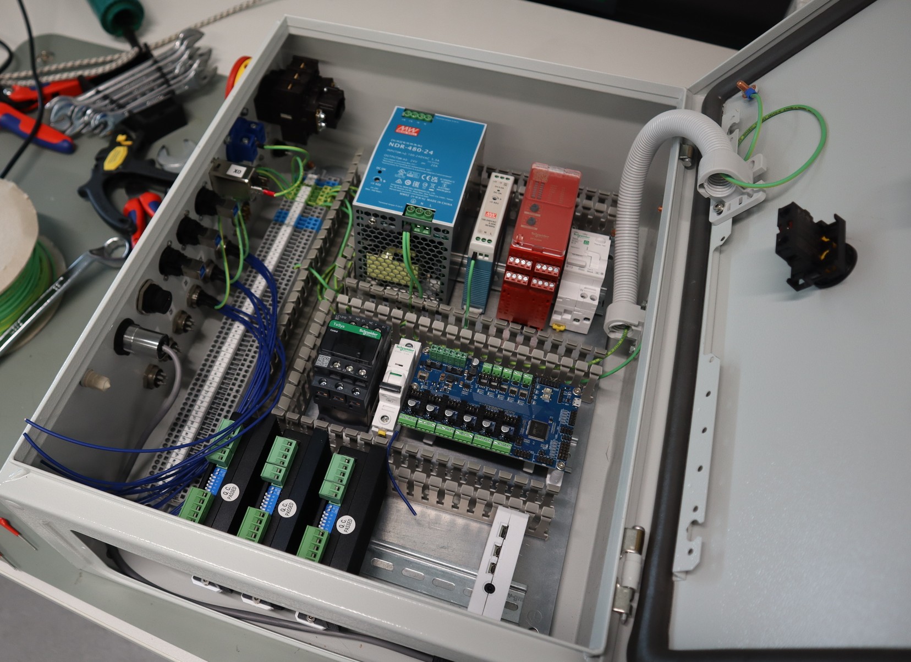
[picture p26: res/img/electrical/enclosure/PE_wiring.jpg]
PE Wiring

---

Figure: PE wiring. The PE wire is connected to the enclosure and all devices inside the enclosure. Compare it to the schematics to see where to connect it.

⚠️**Important**⚠️ Keep the 230V connectors isolated, don't use unisolated connectors like shown in the picture!

### 7. Wire everything else, see [wiring guide](enclosure_wiring.md)

Keep in mind all applicable (local) regulations. 24 V DC is wired in dark blue. 230 V AC is wired in black (not brown like the pictures), the neutral wire is light blue. The 24 V power supply delivers 480 watts, so be aware to choose matching cable diameters.

Additionally, keep the high current motor cables away from the low voltage signal cables to avoid interference.

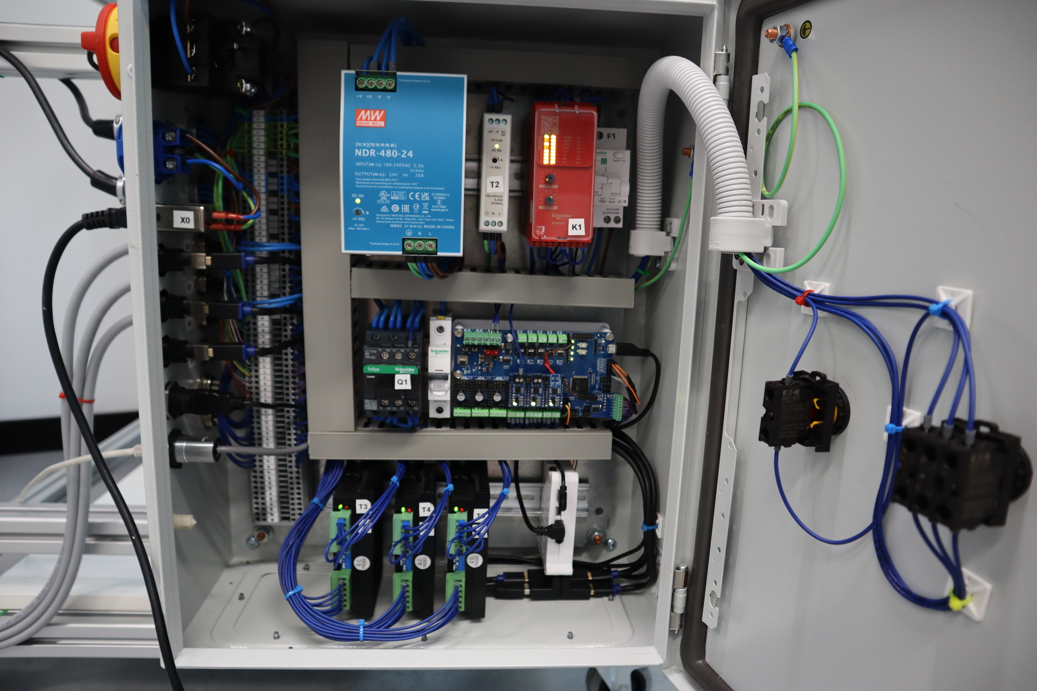
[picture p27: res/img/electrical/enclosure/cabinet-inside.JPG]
Cabinet Inside

Figure: This is an example on how the final wiring can look like.

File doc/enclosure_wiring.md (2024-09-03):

# Schematics and Terminal Plans

<!-- TOC -->

- [Schematics](#schematics)
  - [Power Distribution](#power-distribution)
  - [EmergencyStop](#emergencystop)
    - [Required Specs](#required-specs)
  - [Rumba32 and Motors](#rumba32-and-motors)
    - [NEMA color codes](#nema-color-codes)
  - [RaspberryPi](#raspberrypi)
- [Terminal Plans](#terminal-plans)
  - [X0](#x0)
  - [X1](#x1)
  - [X2](#x2)
  - [X3](#x3)
  - [X4](#x4)
  - [X5](#x5)
  - [X6](#x6)
  - [X7](#x7)
  - [X8](#x8)

<!-- /TOC -->

## Schematics

### Power Distribution

Power Supply Schematic

The contactor $-Q1$ disconnects the motor drivers from the power supply in case of safe-torque-off (aka emergency stop). Schneider Electric has defined this way of wiring in an [application note](https://ckm-content.se.com/ckmContent/sfc/servlet.shepherd/document/download/0691H000008h5vrQAA).

$-F1$ is an overcurrent protection with RCD. Depending to the electric installation of your lab and applicable regional laws it might be optional.

$-F2$ is an overcurrent protection.

### EmergencyStop

It is advisable (and most likely legal obligatory) having a safe-torque-off functionality according to EN-IS0 60204-1 so that the machine can be stopped in case of an emergency. <br>

### Required Specs

- Since the Rumba32 has no failsafe features (SIL-2 or above), the safe-torque-off must be implemented in dedicated hardware.
- To prevent unintended re-start of the drives, a dedicated safety-relais is used (-K1, _XPSUDN13AP_, Schneider Electric). The safety-relais is used with application function '6'. Start function is '1'.
- since there are no stepper motor drivers available with suitable enable inputs (high-active and approved to EN-ISO 60204-1), their enable-inputs can not be used for a safe-torque-off function. So a suitable contactor (DC-3 operation for $20 \ A$ at $24 \ V_{DC}$) must be used to cut-off the power supply to the motor drivers in case of an emergency. This contactor must be selected carefully and wired according to the manufacturers guidelines to ensure safe operation.
- with some bad luck a cheap stepper motor driver can get killed by disrupting the power supply during operation due to the back-EMF of the motor. So a motor driver has to be disabled by the enable pin before interrupting the power supply connection. A 5V signal is sent to the enbable pin of the breakout board if the safety relays turns of. This signal is assumed to be faster than the motors turning off because Q1 is a mechanical relay (switching off the machine by -S0 is always safe: the big $24 \ V$ power supply will slowly turn off the power and eventually take up most of the energy that might return from the drives.)
- The enable input of the motor drivers is used for disabling the drives while performing a field-measurement at an already reached location. This functionality is non safety-relevant, thus it can be implemented the easy way.

Emergency Stop

## Rumba32 and Motors

Rumba32

The [Rumba32](https://github.com/Aus3D/RUMBA32) is a 3D printer board. It is used for time-critical stuff e.g. generate the step and direction pulses for the stepper motor drivers. <br>
The Driver Breakoutboards are little custom PCBs plugged into the Rumba32, [here](rumba32/README.md) is further documentation about them.

### NEMA color codes

NEMA stepper motors usually have short color-coded wires. Unfortunately, there are multiple colorschemes used. However, some widely used color schemes are in the table below:

| Function  | scheme a  | scheme b  | cable core no | motor connector contact   |
| ----      | ----      | ----      | ----          | ---                       |
| A+        | black     |red        | 1             | :5                        |
| A-        | green     |green      | 2             | :4                        |
| B+        | red       |blue       | 3             | :1                        |
| B-        | blue      |yellow     | 4             | :2                        |
| PE/Shield | -         | -         | gn-yl         | :3                        |

Since the cores of the shielded motor cables are black, they have numbers as identifiers. The $cable \ core \ no$ in the table above is referring to the printed identifier on each core of the cable.

## RaspberryPi

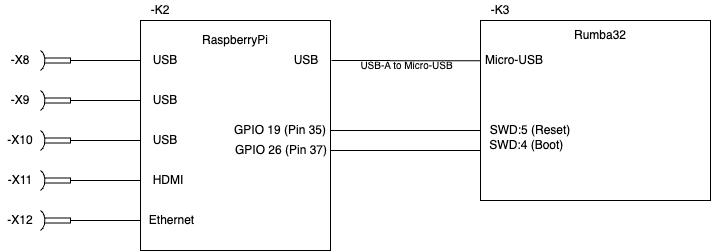
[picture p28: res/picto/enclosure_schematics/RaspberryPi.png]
RaspberryPi


## Terminal Plans

## X0

Mains In Connector (IEC-60320 C13/C14)

| Contact   | connected to  |
| ----      | ----          |
| L         | -S0:3         |
| N         | -S0:5         |
| PE        | -X1:3         |

## X1
<!-- New Contacts:

Additional contacts for
- 8 Hardware limit switches
- 2 Software limit switches
- 5V for the motor enable
-->

|Contact #|Comment              |Bridged to contact |Left             |Right  |
|---------|---------------------|-------------------|-----------------|-------|
|1        | L Mains             | -                 | -F1:2           | -S0:3 |
|2        | N Mains             | -                 | -F1:4           | -S0:6 |
|3        | PE                  | PE DIN-rail       | -X1:24          | -X2:PE|
|4        | PE                  | PE DIN-rail       | -T1:PE          | -X0:PE|
|5        | PE                  | PE DIN-rail       | PE Enclosure    | -X6:3 |
|6        | PE                  | PE DIN-rail       | PE Door         | -X7:3 |
|7        | PE                  | PE DIN-rail       | PE Backplane    | -X8:3 |
|8        | L, fused            | 9                 | -T1:L           |       |
|9        | L, fused            | 8 + 10            | -F1:3           |       |
|10       | L, fused            | 9                 |                 | -X2:L |
|11       | N, fused            | 12                | -T1:N           | -X2:N |
|12       | N, fused            | 11 + 13           | -F1:1           |       |
|13       | N, fused            | 12                |                 |       |
|14       | 5 V                 | 15                | -T2:V+          |       |
|15       | 5 V                 | 14 + 16           | -K2:USB-V+      |       |
|16       | 5 V                 | 14                |                 |       |
|17       | 24 V                | 18                | -F2:1           |       |
|18       | 24 V                | 17 + 19           |                 |       |
|19       | 24 V                | 18 + 20           | -K3:+           | -X4:6 |
|20       | 24 V                | 19                | -K1:13          | -X3:1 |
|21       | 24 V switched       | 22                | -T3:DC+         | -Q1:2 |
|22       | 24 V switched       | 21 + 23           | -T4:DC+         | -Q1:2 |
|23       | 24 V switched       | 22                | -T5:DC+         |       |
|24       | 0 V / PE            | 25                | -X1:3           |       |
|25       | 0 V                 | 24 + 26           | -T1:-V          | -X4:5 |
|26       | 0 V                 | 25 + 27           | -H1:2           |       |
|27       | 0 V                 | 26 + 28           | -T2:-           |       |
|28       | 0 V                 | 27 + 29           | -K1:A2          |       |
|29       | 0 V                 | 28 + 30           | -K2:USB-GND     |       |
|30       | 0 V                 | 29                | -K3:-           | -X5:5 |
|31       | 0 V switched        | 32                | -T3: DC-        | -Q1:L3|
|32       | 0 V switched        | 31 + 33           | -T4:DC-         | -Q1:L3|
|33       | 0 V switched        | 32 + 34           | -T5:DC-         |       |
|34       | 0 V switched        |                   | -T6:DC-         |       |
|35       | ext. Emergency-Stop |                   | -S2:11          | -X3:2 |
|36       | Z+(Hardware)        | -                 | -K1:S13         | -X4:1 |
|37       | Z-(Hardware)        | -                 | -K1:S33         | -X4:2 |
|38       | Y+(Hardware)        | -                 | -K1:S53         | -X4:3 |
|39       | Y-(Hardware)        | -                 | -K1:S23         | -X4:4 |
|40       | X+(Hardware)        | -                 | -K1:S43         | -X4:7 |
|41       | X-(Hardware)        | -                 | -K1:S63         | -X4:8 |
|42       | Z+(Software)        | -                 | -K3:Z+          | -X5:1 |
|43       | Z-(Software)        | -                 | -K3:Z-          | -X5:2 |
|44       | Y+(Software)        | -                 | -K3:Y+          | -X5:3 |
|45       | Y-(Software)        | -                 | -K3:Y-          | -X5:4 |
|46       | X+(Software)        | -                 | -K3:X+          | -X5:7 |
|47       | X-(Software)        | -                 | -K3:X-          | -X5:8 |
|48       | 12 V Endstop        |                   | -K3:12V Endstops| -X5:6 |
|49       | -M1:A+              |                   | -T3:A+          | -X6:5 |
|50       | -M1:A-              |                   | -T3:A-          | -X6:4 |
|51       | -M1:B+              |                   | -T3:B+          | -X6:1 |
|52       | -M1:B-              |                   | -T3:B-          | -X6:2 |
|53       | -M2:A+              |                   | -T4:A+          | -X7:5 |
|54       | -M2:A-              |                   | -T4:A-          | -X7:4 |
|55       | -M2:B+              |                   | -T4:B+          | -X7:1 |
|56       | -M2:B-              |                   | -T4:B-          | -X7:2 |
|57       | -M3:A+              |                   | -T5:A+          | -X8:5 |
|58       | -M3:A-              |                   | -T5:A-          | -X8:4 |
|59       | -M3:B+              |                   | -T5:B+          | -X8:1 |
|60       | -M3:B-              |                   | -T5:B-          | -X8:2 |
|61       |                     |                   |                 |       |
|62       |                     |                   |                 |       |
|63       |                     |                   |                 |       |
|64       |                     |                   |                 |       |
|65       |                     |                   |                 |       |
|66       |                     |                   |                 |       |
|67       |                     |                   |                 |       |
|68       |                     |                   |                 |       |
|69       |                     |                   |                 |       |
|70       |                     |                   |                 |       |

The contacts 61 to 70 are reserved for future upgrades, e.g. additional axis.

## X2

External Power Socket

| Contact   | connected to  |
| ----      | ----          |
| L         | -X1:10        |
| N         | -X1:11        |
| PE        | -X1:7         |

## X3

External Emergency Stop Connector

| Contact | Comment     | Connected To |
|---------|-------------|--------------|
| 1       | +24 V       | -X1:19       |
| 2       | Switch Out  | -X1:35       |
| 3       | -           | -            |

## X4

Hardware Endstops Connector 10 pin

| Contact | Comment    | Connected To |
|---------|------------|--------------|
| 1       | Z+         | -X1:35       |
| 2       | Z-         | -X1:36       |
| 3       | Y+         | -X1:38       |
| 4       | Y-         | -X1:39       |
| 5       | 0 V        | -X1:24       |
| 6       | 24V        | -X1:18       |
| 7       | X+         | -X1:40       |
| 8       | X-         | -X1:41       |
| 9       | -          | -            |
| 10      | -          | -            |

## X5

Software Endstops Connector 10 PIN

| Contact | Comment | Connected To |
|---------|---------|--------------|
| 1       | Z+      | -X1:42       |
| 2       | Z-      | -X1:43       |
| 3       | Y+      | -X1:44       |
| 4       | Y-      | -X1:45       |
| 5       | 0V      | -X1:29       |
| 6       | 12 V    | -X1:37       |
| 7       | X+      | -X1:46       |
| 8       | X-      | -X1:47       |
| 9       | -       | -            |
| 10      | -       | -            |

## X6

Motor X-Axis Connector (GX20 5-pin)

| Contact | Comment     | Connected To |
|---------|-------------|--------------|
| 1       | B+          | -X1:50       |
| 2       | B-          | -X1:51       |
| 3       | PE & Shield | -X1:5        |
| 4       | A-          | -X1:49       |
| 5       | A+          | -X1:48       |

## X7

Motor Y-Axis Connector (GX20 Shieled 5-pin)

| Contact | Comment     | Connected To |
|---------|-------------|--------------|
| 1       | B+          | -X1:54       |
| 2       | B-          | -X1:55       |
| 3       | PE & Shield | -X1:6        |
| 4       | A-          | -X1:53       |
| 5       | A+          | -X1:52       |

## X8

Motor Z-Axis Connector (GX20 Shielded 5 pin)

| Contact | Comment     | Connected To |
|---------|-------------|--------------|
| 1       | B+          | -X1:58       |
| 2       | B-          | -X1:59       |
| 3       | PE & Shield | -X1:7        |
| 4       | A-          | -X1:57       |
| 5       | A+          | -X1:56       |

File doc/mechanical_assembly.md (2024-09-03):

# COSI Measure Assembly

This document contains the steps to assemble the mechanical components of the COSI measure. The mechanical assembly is the first step in the assembly process. Once you have completed the mechanical assembly, you can move on to the [Enclosure Assembly](enclosure_assembly.md).

## Table of Contents

1. [Introduction](#introduction)
2. [Ordering Parts and Build Notes](#ordering-parts-and-build-notes)
3. [Assembly](#assembly)
4. [Testing](#testing)

## Introduction

We have two different assemblies to do, the mechanical assembly and the electrical assembly. The mechanical assembly is straightforward - just follow the assembly instructions.

For the electrical part some PCBs have to be manufactured and you should probably have some experience with wiring electronics.

## Ordering Parts and Build Notes

The BOM for the mechanical parts can be found [here](../src/mechanical/2024-08-03_cosi-measure_v2.0_BoM_mechanical_assembly.md). You need to manufacture some parts, like the aluminum plates, and order some parts, like the linear bearings.

Technical drawings for the aluminum plates can be found [here](../src/mechanical/Aluplates/FreeCAD/Technical%20Drawings).

The links in the BOM are still valid, so you can use them to order the parts (April-2024).

Make sure to order a few extra screws and nuts, since you don't want to be stuck in the middle of the assembly process because you are missing a screw.

The final assembly is quite large, so make sure you can still transport it to the place where you want to use it.

## Assembly

### Mechanical Assembly

#### Step 1

| Quantity | Part description              | BoM Number | Comment |
|----------|-------------------------------|------------|---------|
| 6        | Aluminum Frames (40x80x800)mm | 1          |         |
| 8        | Angles, 40x80                 | 2          |         |
| 36       | Slot nuts, M8                 | 2/4        |         |
| 32       | Screws, M8x18                 | 2          |         |

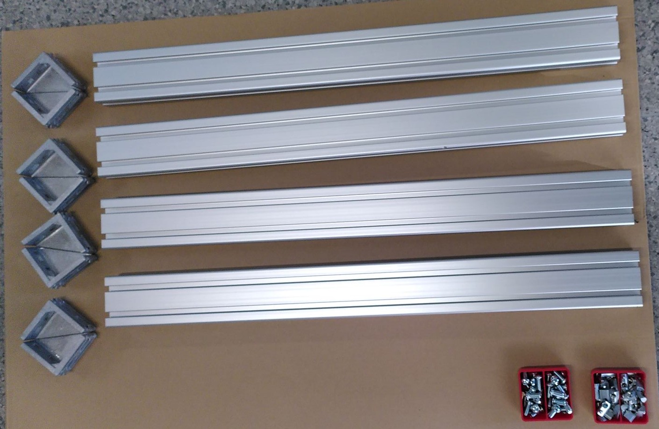
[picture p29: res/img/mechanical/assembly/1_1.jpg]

<figcaption>Figure 1: Components needed for step 1. Two aluminum profiles are missing in the picture. </figcaption>

---

1.1. Insert the _Slot nuts, M8_ into the _Aluminum Frames (40x80x800)mm_.

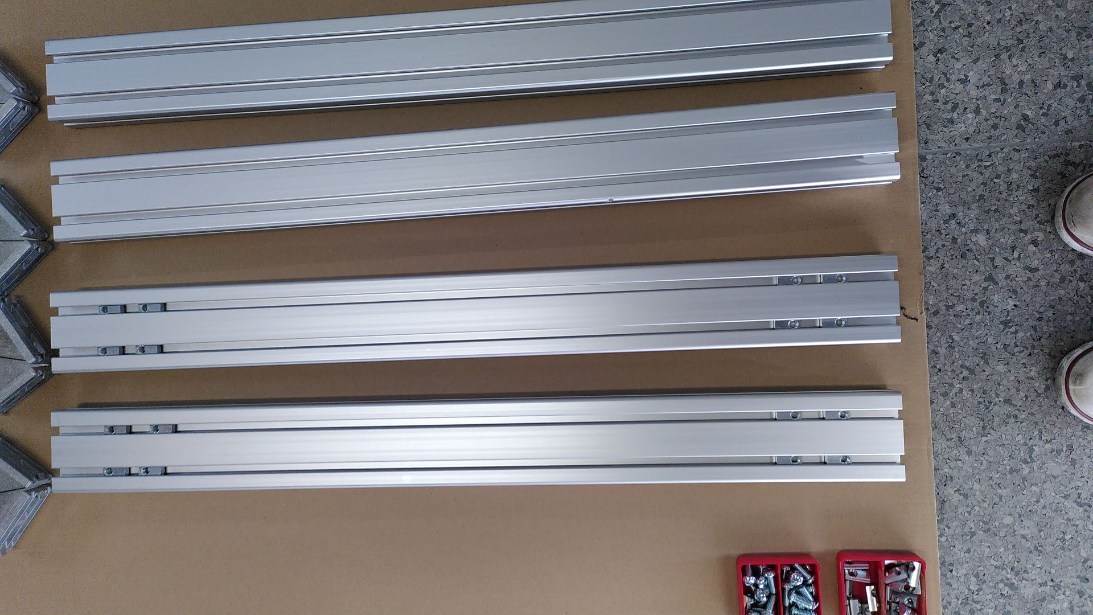
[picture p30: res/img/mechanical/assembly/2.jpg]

<figcaption>Figure 1.1: Inserted slots for two of the aluminum frames. Do this for all 6 parts.    </figcaption>

---

1.2 Add _Angles, 40x80_ to two of the _Aluminum Frames (40x80x800)mm_ using the _Screws, M8x18_ and the previously inserted _Slot nuts, M8_. I placed the _Angles, 40x80_ with the bridge facing each other to avoid forming a hard to clean cavity.

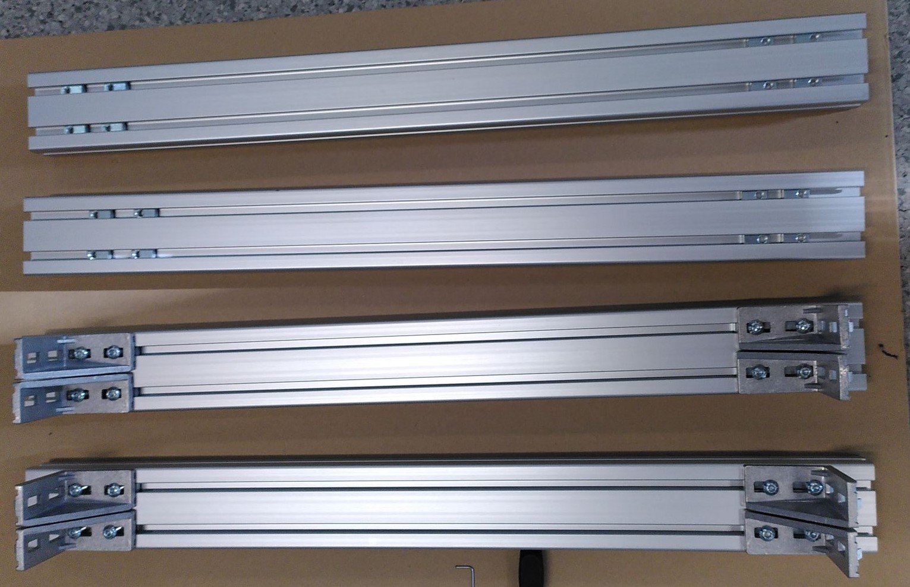
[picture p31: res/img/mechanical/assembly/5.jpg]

<figcaption> Figure 1.2: Aluminium frames with the the angles mounted.</figcaption>

---

1.3 Take four _Slot nuts, M8_ and insert them into the _Aluminum Frames (40x80x800)mm_ with the mounted angles. Do this on the short side, perpendicular to where you placed the slot nuts in the aluminum frames previously.

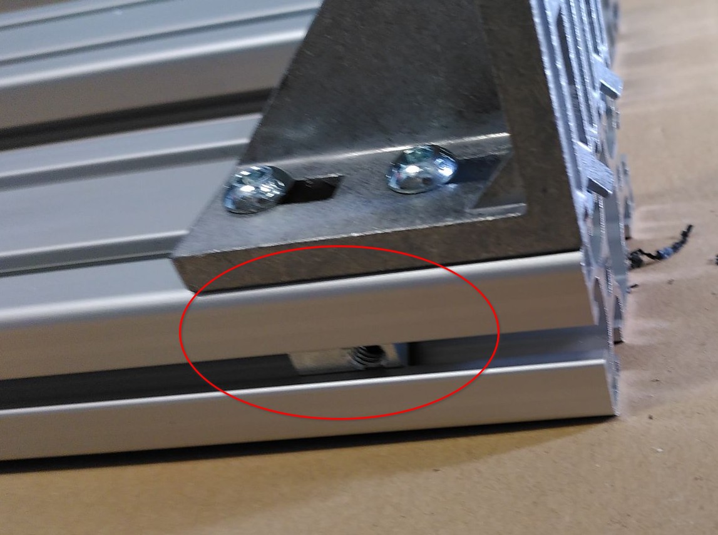
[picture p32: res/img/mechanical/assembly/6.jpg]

<figcaption> Figure 1.3: Slot nuts inserted into the angles. </figcaption>

---

1.4 Form a U shape with the frame with the angle mounted and two of the frames without angles. Do this twice to obtain two U shapes.

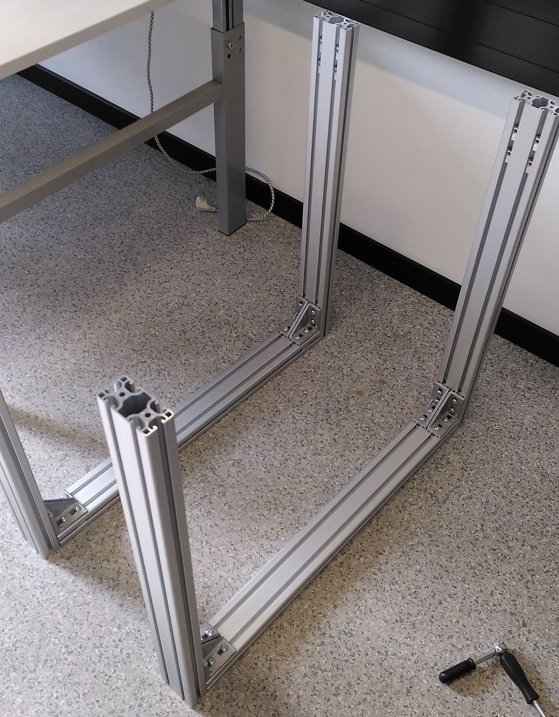
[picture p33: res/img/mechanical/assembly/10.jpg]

<figcaption> Figure 1.4: U shape formed with the frames. </figcaption>

---

#### Step 2

| Quantity | Part description              | BoM Number | Comment |
|----------|-------------------------------|------------|---------|
| 2        | Aluminum Frames (40x40x800)mm | 3          |         |
| 8        | Angles, 40x40                 | 4          |         |
| 12       | Slot nuts, M8                 | 4          |         |
| 16       | Screws, M8x16, countersunk    | 4          |         |

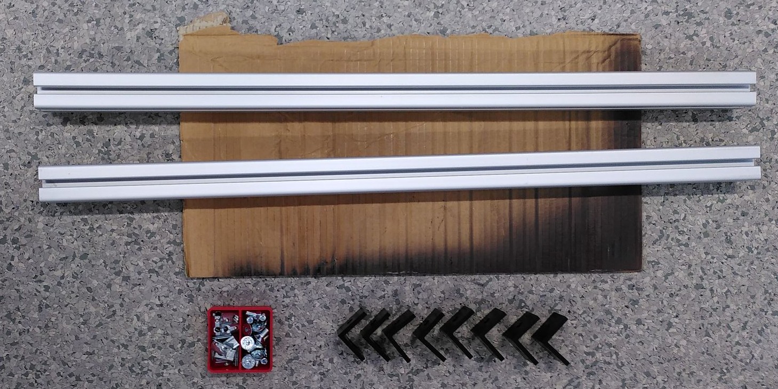
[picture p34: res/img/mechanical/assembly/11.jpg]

<figcaption> Figure 2: Components needed for step 2. </figcaption>

---

2.1 Add two _Slot nuts, M8_ to the _Aluminum Frames (40x40x800)mm_ in a perpendicular fashion.

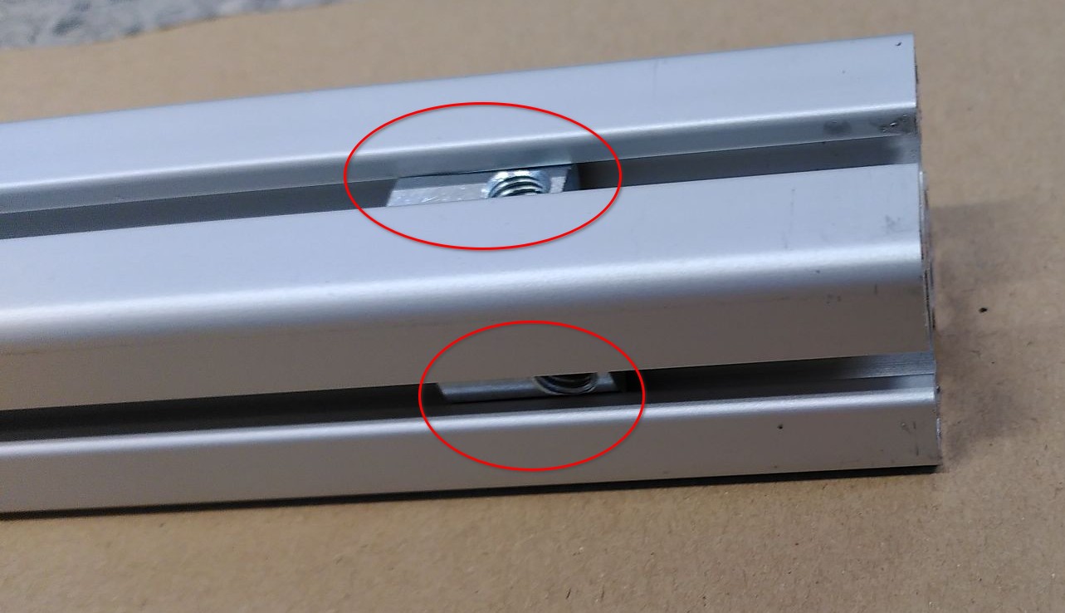
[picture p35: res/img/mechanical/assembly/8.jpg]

<figcaption> Figure 2.1: Slot nuts inserted into the aluminum frame. Do this for both sides for both aluminum frames. </figcaption>

---

2.2 Connect the _Aluminum Frames (40x40x800)mm_ with the _Angles, 40x40_ using the _Screws, M8x16, countersunk_. Then use the _Aluminum Frames (40x40x800)mm_ with the _Angles, 40x40_ attached, to connect the U shapes from step 1.

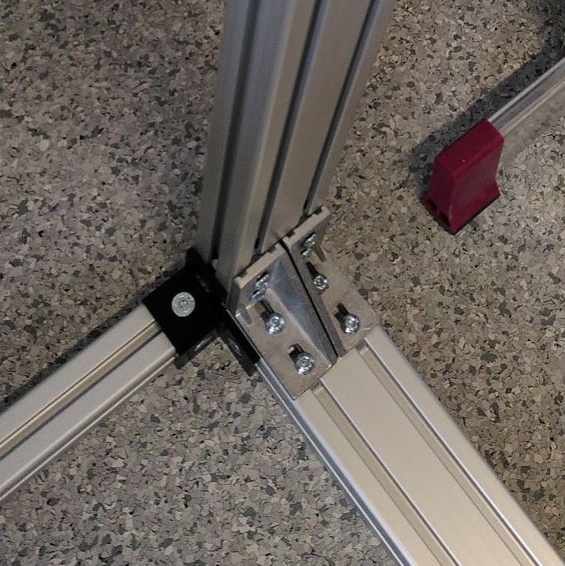
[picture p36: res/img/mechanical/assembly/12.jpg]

<figcaption> Figure 2.2: Aluminum frames connected with the angles. </figcaption>

#### Step 3

| Quantity | Part description | BoM Number | Comment |
|----------|------------------|------------|---------|
| 18       | Slot nuts, M8    | 4          |         |

---

3.1 Add the _Slot nuts, M8_ to the top of the upright standing aluminum frames (inner side).

#### Step 4

| Quantity | Part description               | BoM Number | Comment |
|----------|--------------------------------|------------|---------|
| 18       | Slot nuts, M8                  | 4          |         |
| 2        | Aluminum frames, (40x80x880)mm | 5          |         |
| 8        | Angles, 40x80                  | 2          |         |
| 32       | Screws, M8x18                  | 2          |         |
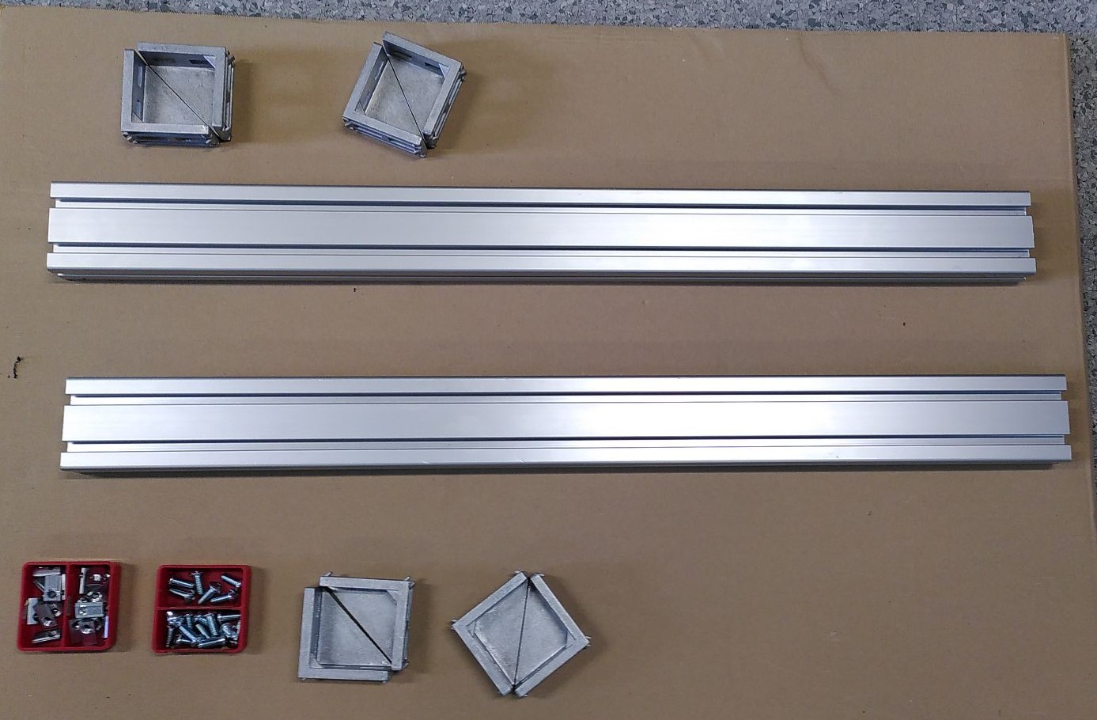
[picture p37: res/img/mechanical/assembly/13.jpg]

<figcaption> Figure 4: Components needed for step 4. </figcaption>

---

4.1 We add the _Slot nuts, M8_ to the _Aluminum frames, (40x80x880)mm_. Four on each side on the long side. On the short (perpendicular) side we add two _Slot nuts, M8_.

4.2 Attach the _Angles, 40x80_ to the _Aluminum frames, (40x80x880)mm_ using the _Screws, M8x18_.

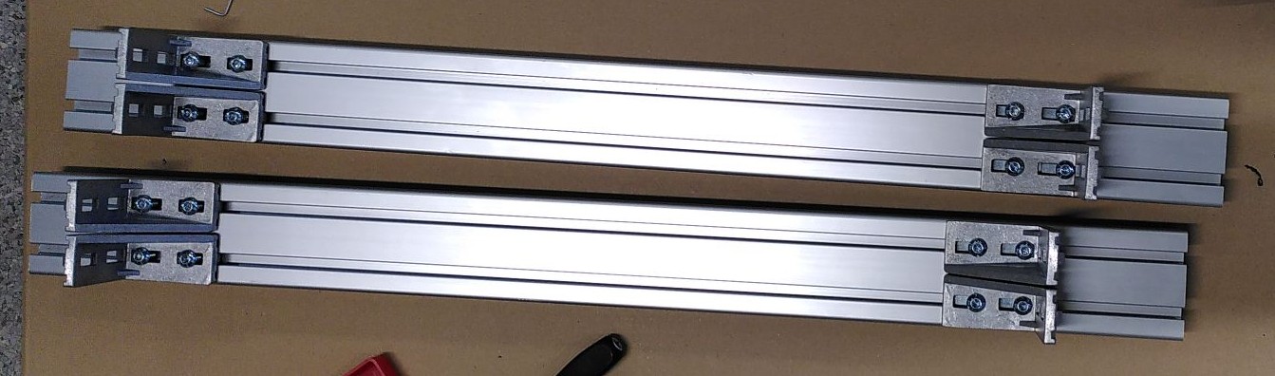
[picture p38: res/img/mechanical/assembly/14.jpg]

<figcaption> Figure 4.2: Angles attached to the aluminum frames. </figcaption>

---

4.3 Attach the _Angles, 40x80_ to the U shapes from step 2 using the _Screws, M8x18_.
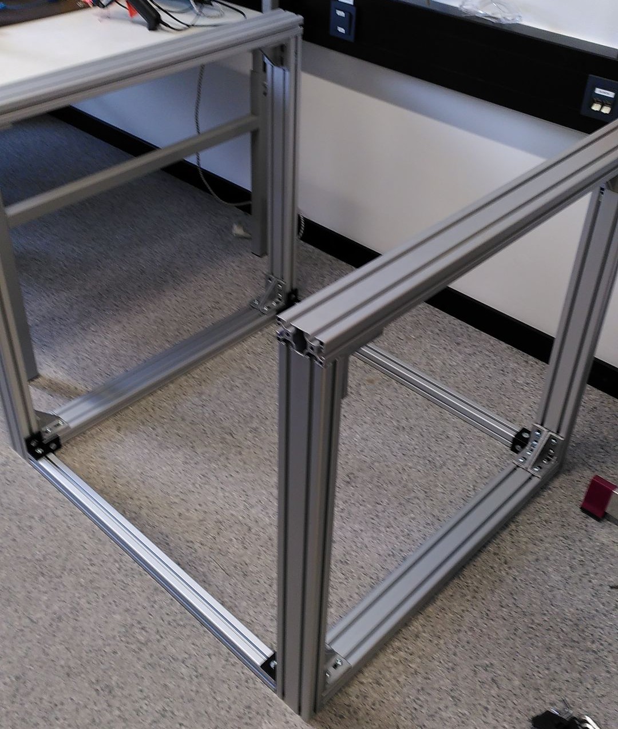
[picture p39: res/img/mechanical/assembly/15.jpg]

<figcaption> Figure 4.3: U shapes connected to the aluminum frames. </figcaption>

---

#### Step 5

| Quantity | Part description               | BoM Number | Comment |
|----------|--------------------------------|------------|---------|
| 1        | Aluminum frame, (40x40x800)mm | 3          |         |
| 8        | Screws, M8x16, countersunk     | 4          |         |
| 4        | Slot nuts, M8                  | 4          |         |
| 4        | Angles, 40x40                  | 4          |         |
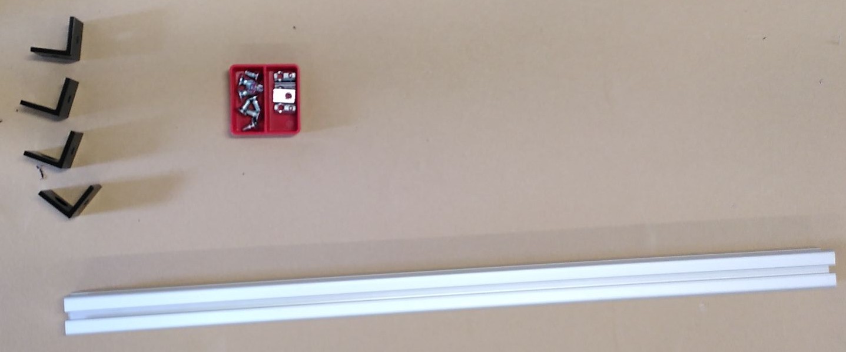
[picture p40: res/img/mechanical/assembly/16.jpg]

<figcaption> Figure 5: Components needed for step 5. </figcaption>

---

5.1 Add the _Slot nuts, M8_ to the _Aluminum frame, (40x40x800)mm_ similar to Figure 2.1.

5.2 Use the angles to connect the _Aluminum frame, (40x40x800)mm_ to backside of the assembled structure.

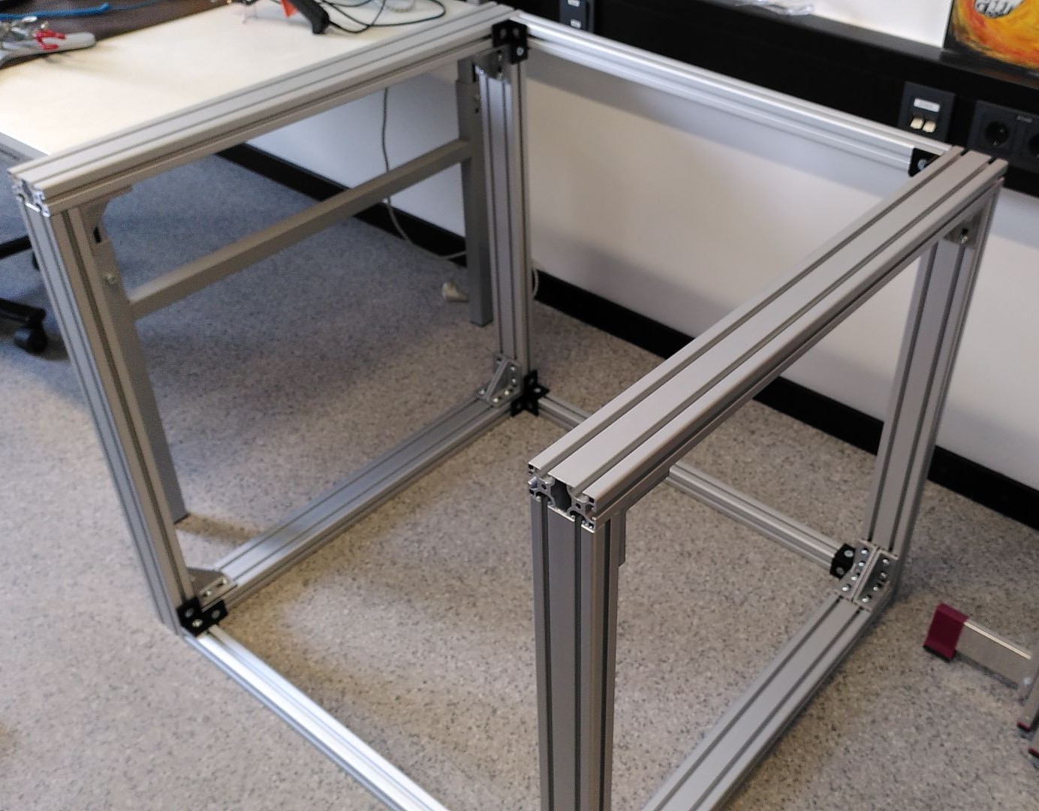
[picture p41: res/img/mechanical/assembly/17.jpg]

<figcaption> Figure 5.2: Aluminum frame (40x40x800)mm attached to the backside of the structure. </figcaption>

---

##### Optional Step

If you want to attach the electronics cabinet to the aluminum frame, you can add two additional _Aluminum frames, (40x40x800)mm_ to the left side of the structure. Make sure to have a distance between the two aluminum profiles that is equal to the mounting holes of the electronics cabinet.

| Quantity | Part description               | BoM Number | Comment |
|----------|--------------------------------|------------|---------|
| 8        | Slot nuts, M8                  | (optional) |         |
| 2        | Aluminum frame, (40x40x800)mm  | (optional) |         |
| 8        | Screws, M8x16, countersunk     | (optional) |         |

---

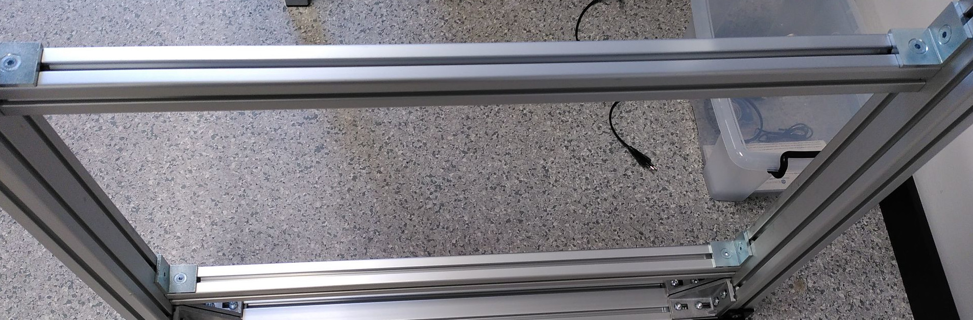
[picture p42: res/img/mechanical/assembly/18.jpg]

<figcaption> Figure 5.3: Aluminum frame (40x40x800)mm attached to the left side of the structure for mounting of the electronics cabinet. </figcaption>

---

You might want to loosen the upper screws of the aluminum frame to slide the aluminum profiles in.

You can also flip the structure to the side and place the electronics cabinet on th the aluminum profiles the check if the mounting holes align.

If you want the final assembly to be a little less broad, you can also add the _Aluminum frames, (40x40x800)mm_ to the inner side of the structures _Aluminum frames, (40x80x800)mm_.

---

#### Step 6

Now we will attach the plates for the y-axis motor and spindle. Note: the pictures are without the optional step.

| Quantity | Part description               | BoM Number | Comment |
|----------|--------------------------------|------------|---------|
| 10       | Slot nuts, M8                  | 5          |         |
| 1        | Aluminum plate 3               | 6          | See [Technical Drawing](../src/mechanical/Aluplates/FreeCAD/Technical%20Drawings/2018-08-02_COSImeasure_mechanical_plate3.pdf)         |
| 1        | Aluminum plate 4               | 6          | See [Technical Drawing](../src/mechanical/Aluplates/FreeCAD/Technical%20Drawings/2018-08-02_COSImeasure_mechanical_plate4.pdf)         |
| 10         | Screws, M8x20, countersunk  | 7          |         |

---

6.1 Insert the 6 _Slot nuts, M8_ into the aluminum frame on the "left back side" of the structure.

6.2 Insert the 4 _Slot nuts, M8_ into the aluminum frame on the "right side" of the structure.

---

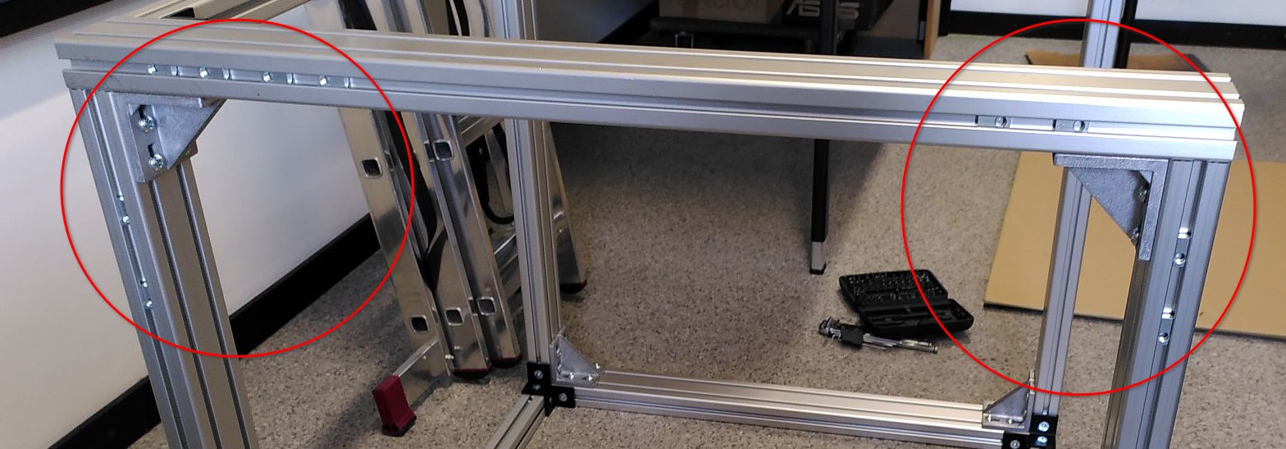
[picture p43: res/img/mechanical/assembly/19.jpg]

<figcaption> Figure 6: The Slot nuts, M8 that have been added to the aluminum frames are marked in red. </figcaption>

---

6.3 Attach the _Aluminum plate 3_ to the aluminum frame on the "left back side" of the structure using the _Screws, M8x20, countersunk_.

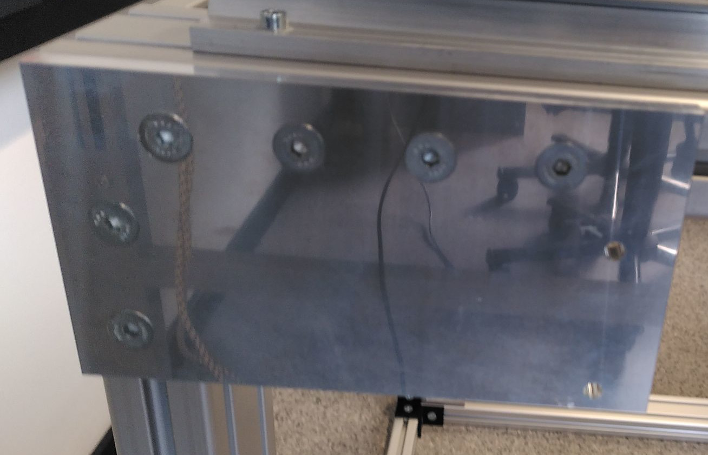
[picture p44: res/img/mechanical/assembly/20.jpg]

<figcaption> Figure 6.3: Aluminum plate 3 attached to the aluminum frame. </figcaption>

---

6.4 Attach the _Aluminum plate 4_ to the aluminum frame on the "right side" of the structure using the _Screws, M8x20, countersunk_.

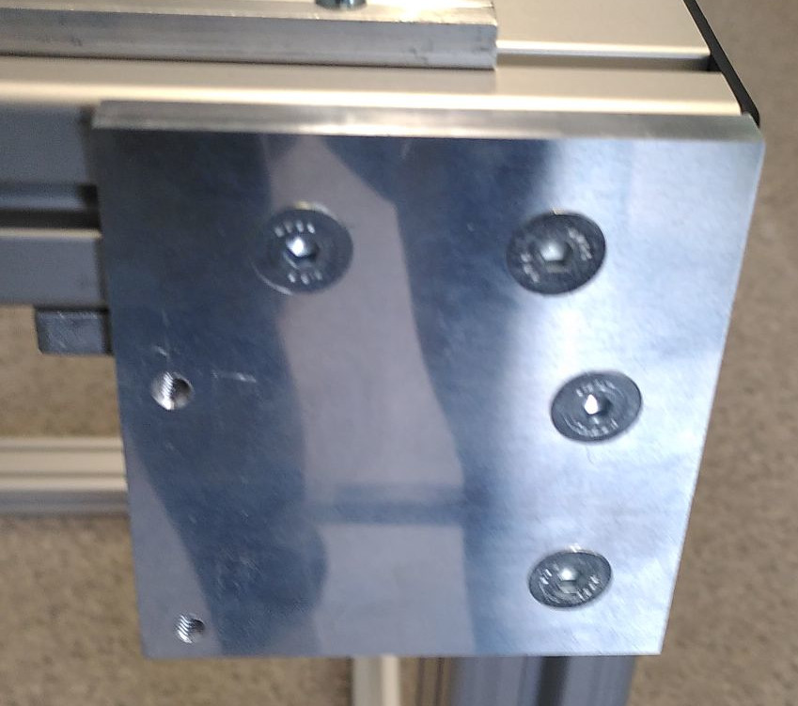
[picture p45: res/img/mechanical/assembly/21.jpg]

<figcaption> Figure 6.4: Aluminum plate 4 attached to the aluminum frame. </figcaption>

---

#### Step 7

| Quantity | Part description               | BoM Number | Comment |
|----------|--------------------------------|------------|---------|
| 24       | Slot nuts, M5                  | 8          |         |
| 2        | Supported rail, TBS20          | 9          |         |
| 24       | Screws, M5x20                  | 10         |         |
|4         | Linear bearing, TBR20UU        | 11         |         |
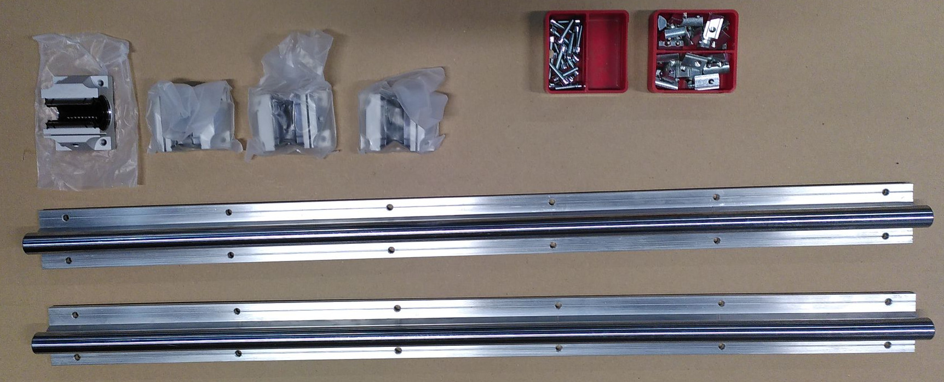
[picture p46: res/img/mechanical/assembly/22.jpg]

<figcaption> Figure 7.2: Components needed for step 7 </figcaption>

---

7.1 Insert the _Slot nuts, M5_ into top aluminum frame (24 in total).

7.2 Attach the _Supported rail, TBS20_ to the top aluminum frame using the _Screws, M5x20_. **Don't tighten the screws yet.**

7.3 Slide the _Linear bearing, TBR20UU_ into the _Supported rail, TBS20_.

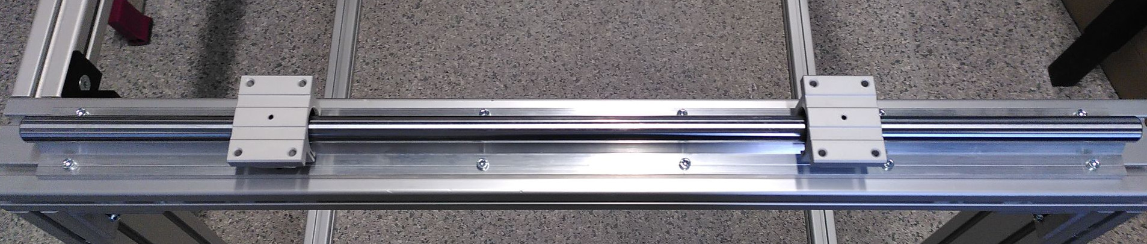
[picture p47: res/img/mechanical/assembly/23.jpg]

<figcaption> Figure 7.3: Supported rail attached to the top aluminum frame. </figcaption>

---

#### Step 8

Now the spindle block with the motor holder will be assembled for the x and y-axis (Easy-Mechatronics System).

| Quantity | Part description               | BoM Number | Comment |
|----------|--------------------------------|------------|---------|
| 2        | Ballscrew & spindle nut block  | 12         |         |
| 2        | Fixed bearing & motor holder   | 13         |         |
| 2        | Floating bearing               | 14         |         |
| 2        | Motor coupler                  | 15         |         |

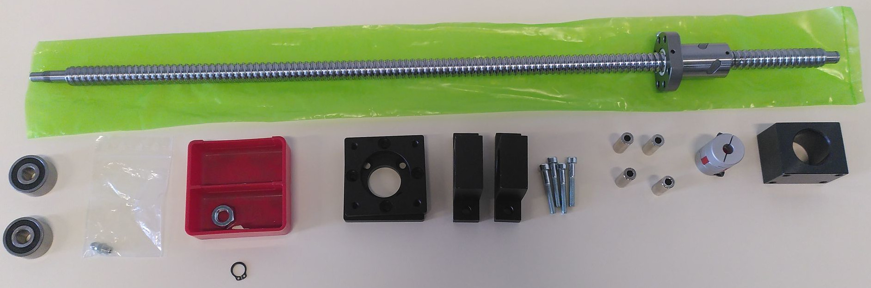
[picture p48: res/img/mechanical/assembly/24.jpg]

<figcaption> Figure 8: Components needed for step 8. These are only for one of the axes, so you will need all components twice. You will need some additional screws for assembly of the spindle block.</figcaption>

---

8.1 You can find assembly instructions for the assembly of the Easy-Mechatronics system block in [this video](https://invidious.private.coffee/watch?v=Gt8ER-_8GjY). The spindle block itself needs to be assembled differently in comparison to the video. Instructions for the spindle block assembly can be found [here](https://invidious.private.coffee/watch?v=TItAG3wGPzI).
The grease fitting should be on the upper side of the spindle block for one of the axes and on the lower side for the other axis. This makes sure the grease fitting is accessible after the assembly of the complete system.

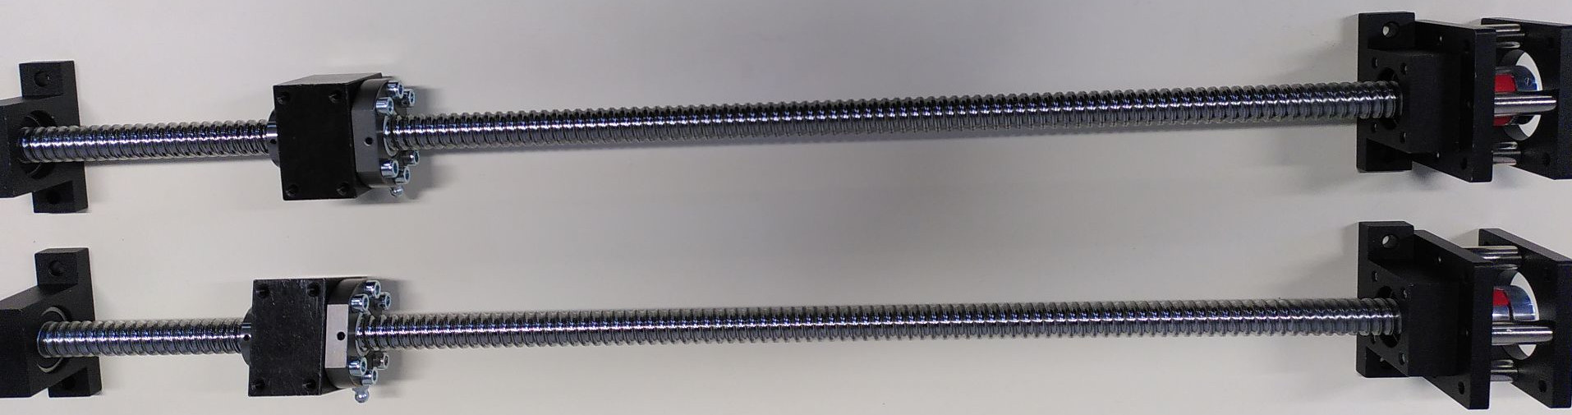
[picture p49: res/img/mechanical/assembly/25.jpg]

<figcaption> Figure 8.1: Assembled Easy-Mechatronics System for the x and y axis. </figcaption>

---

#### Step 9

Now we will build the z-axis.

| Quantity | Part description               | BoM Number | Comment |
|----------|--------------------------------|------------|---------|
| 1        | Easy-Mechatronics System       | 16         |         |
| 1        | Aluminum plate 8               | 6          | See [Technical Drawing](../src/mechanical/Aluplates/FreeCAD/Technical%20Drawings/2018-08-02_COSImeasure_mechanical_plate8.pdf) |
| 1        | Aluminum plate 9               | 6          | See [Technical Drawing](../src/mechanical/Aluplates/FreeCAD/Technical%20Drawings/2018-08-02_COSImeasure_mechanical_plate9.pdf) |
| 12      | Screws, M6x20               | 17          |         |

---

9.1 Assemble the Easy-Mechatronics System for the z-axis just as you did for the x and y-axis. Make sure the grease fitting is accessible after the assembly of the complete system.

9.2 Attach the _Aluminum plate 8_ and _Aluminum plate 9_  to the Easy-Mechatronics System for the z-axis using the _Screws, M6x20_. Make sure you have the correct orientation: The motor holder is on the smaller _Aluminum plate 8_.

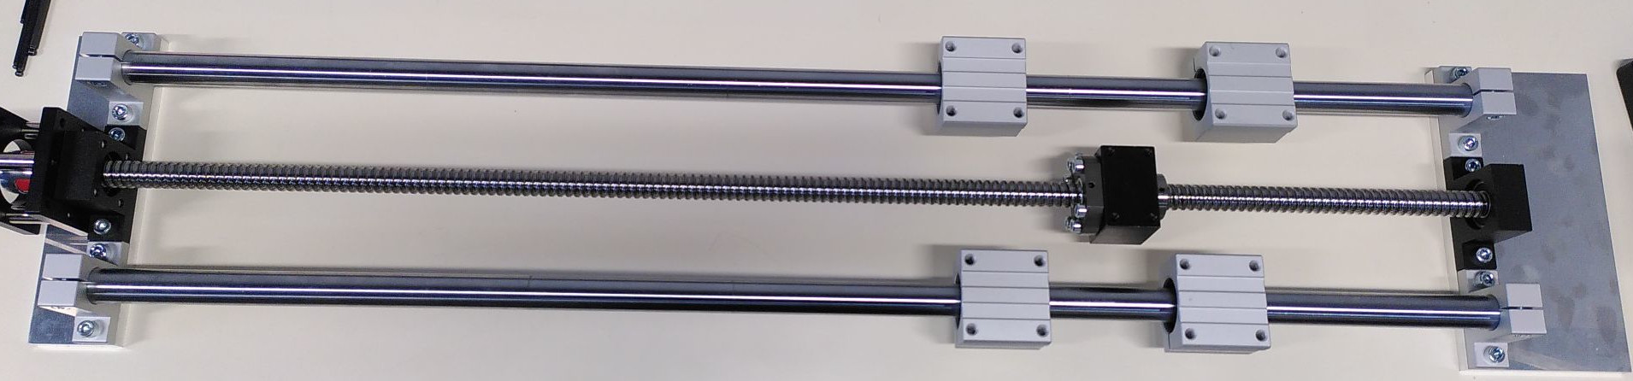
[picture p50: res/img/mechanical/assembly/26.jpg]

<figcaption> Figure 9.2: Assembled Easy-Mechatronics System for the z-axis. </figcaption>

---

#### Step 10

Now we will attach the x and y-axis to the structure.

| Quantity | Part description               | BoM Number | Comment |
|----------|--------------------------------|------------|---------|
| 1        | Aluminum Plate 1               | 6          | See [Technical Drawing](../src/mechanical/Aluplates/FreeCAD/Technical%20Drawings/2018-08-02_COSImeasure_mechanical_plate1_2of2.pdf)
| 16       | Screws, M6x20, countersunk    | 18         |         |
| 2        | Assembly of x and y-axis      |          | See step 8|

| 6        | Screws, M6x20                 | 17         |         |
| 2        | Screws, M6x30                 | 24         |         |
| 2        | Screw nuts, M6                | 25         |         |

---

10.1 Attach the _Aluminum Plate 1_ to four linear bearings using the _Screws, M6x20, countersunk_.

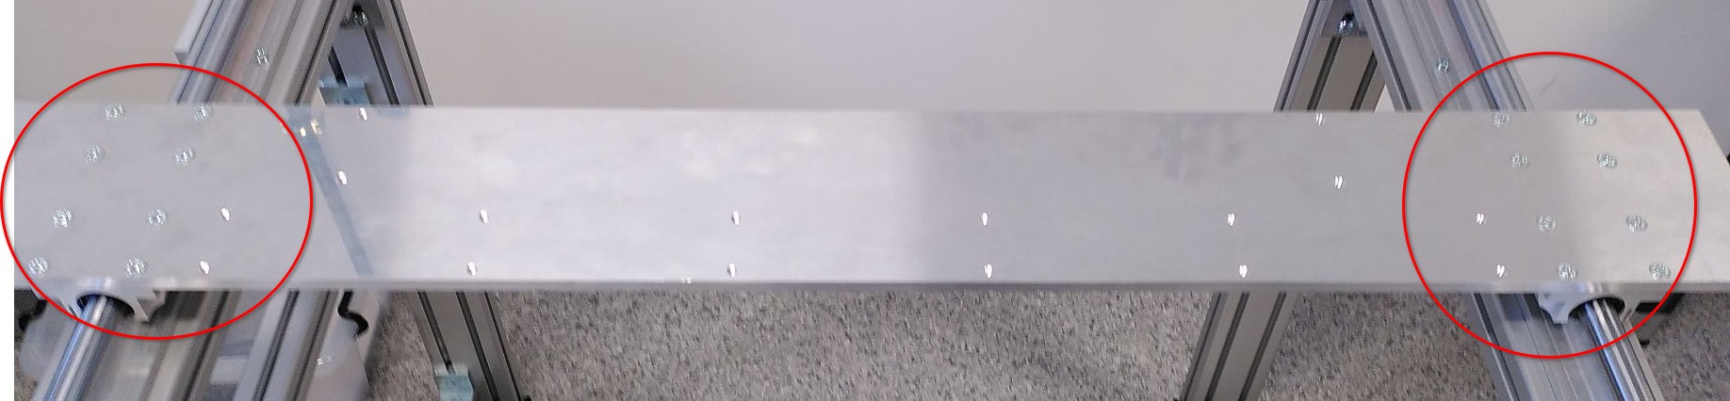
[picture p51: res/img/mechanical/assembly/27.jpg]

<figcaption> Figure 10.1: Aluminum Plate 1 attached to the linear bearings. </figcaption>

---

10.2 Attach the x-axis to _Aluminum Plate 1_ using the _Screws, M6x20_. Make sure to orient the motor correctly. It makes sense to have the motor on the side of the electronics cabinet. You don't need to mount the motor yet.

<p float="left">
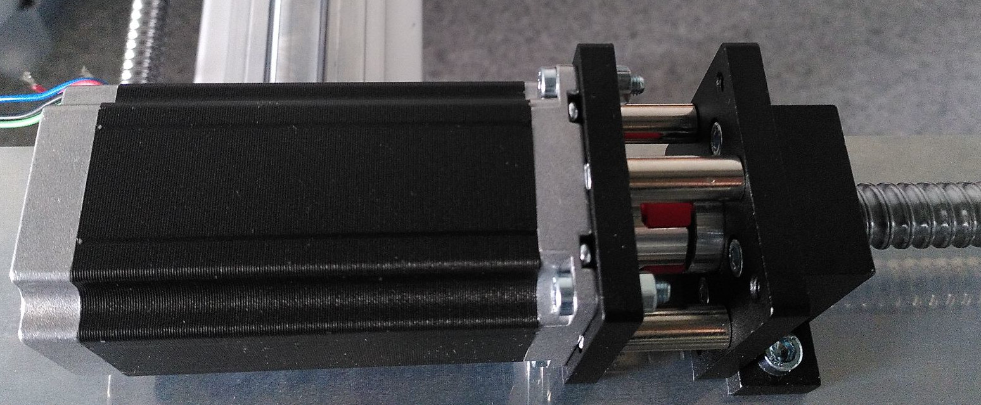
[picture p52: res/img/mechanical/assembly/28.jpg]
  
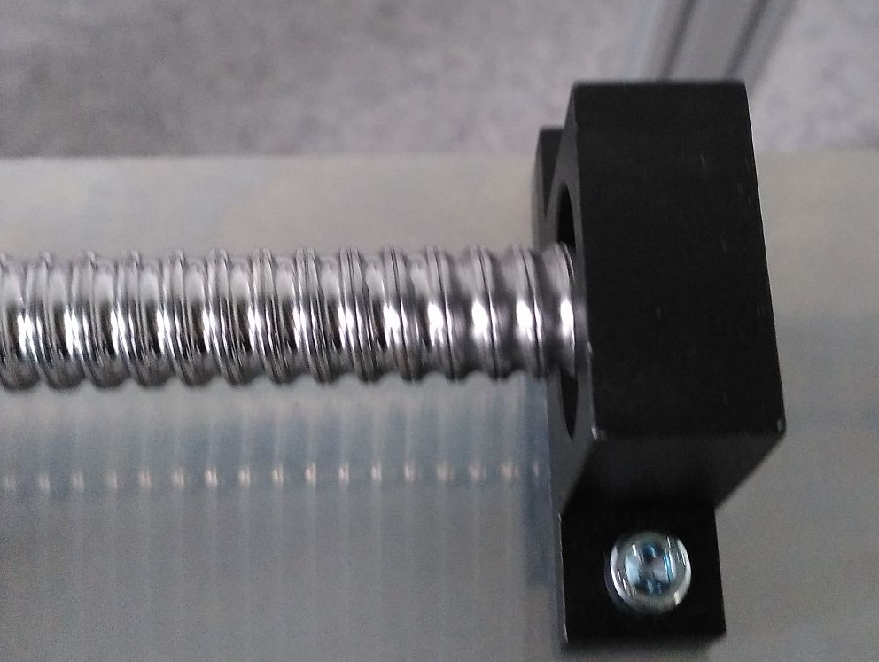
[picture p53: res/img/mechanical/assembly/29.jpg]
  
</p>

---

10.3 Attach the y-axis to the _Aluminum Plate 3_ using the _Screws, M6x30_ together with the _Screw nuts, M6_ (motor side). Attach the other side of the y-axis to the _Aluminum Plate 4_ using the _Screws, M6x20_.

<p float="left">
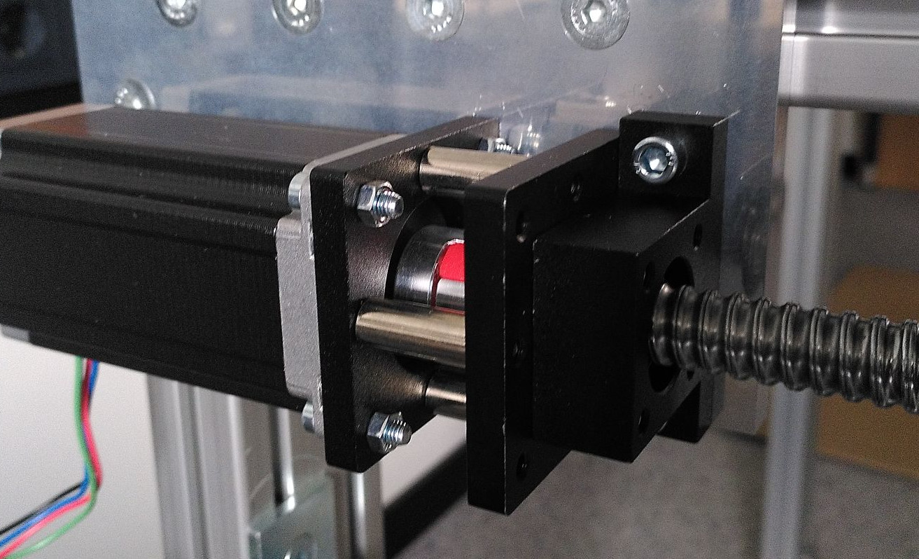
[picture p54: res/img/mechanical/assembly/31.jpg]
  
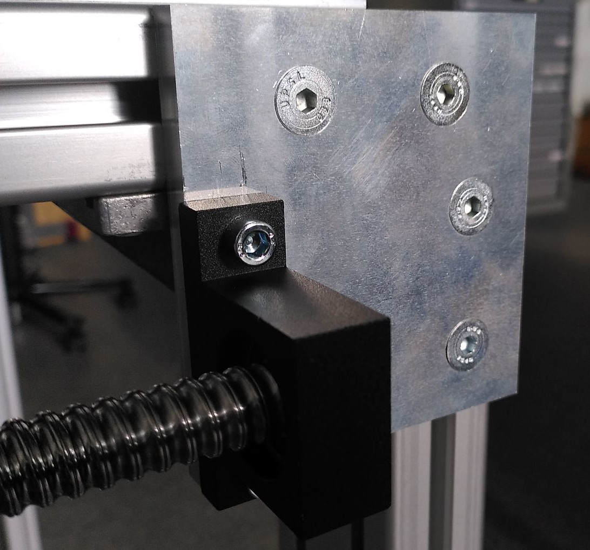
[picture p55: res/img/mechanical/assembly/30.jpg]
  
</p>

---

#### Step 11

We now assemble the carriage for the z-axis.

| Quantity | Part description               | BoM Number | Comment |
|----------|--------------------------------|------------|---------|
| 1        | Aluminum Plate 5               | 6          | See [Technical Drawing](../src/mechanical/Aluplates/FreeCAD/Technical%20Drawings/2018-08-02_COSImeasure_mechanical_plate5.pdf) |
| 1        | Aluminum Plate 6               | 6          | See [Technical Drawing](../src/mechanical/Aluplates/FreeCAD/Technical%20Drawings/2018-08-02_COSImeasure_mechanical_plate6.pdf) |
| 1        | Aluminum Plate 7               | 6          | See [Technical Drawing](../src/mechanical/Aluplates/FreeCAD/Technical%20Drawings/2018-08-02_COSImeasure_mechanical_plate7.pdf) |
| 4       | Screws, M5x30                 | 19         |         |
| 16      | Screws, M6x20, countersunk    | 18         |         |
| 4       | Screws, M5x30, countersunk    | 24         |         |

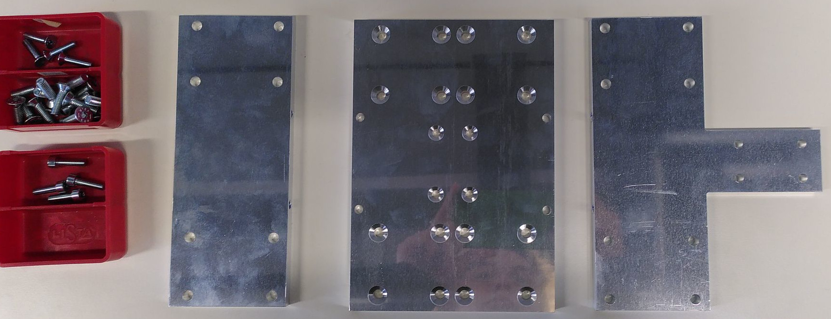
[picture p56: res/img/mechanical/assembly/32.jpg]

<figcaption> Figure 11: Components needed for step 11. </figcaption>

---

11.1 Connect _Aluminum Plate 5_ to _Aluminum Plate 6_ using the _Screws, M5x30_.

11.2 Connect _Aluminum Plate 6_ to _Aluminum Plate 7_ using the _Screws, M6x30. The assembly should look like this:

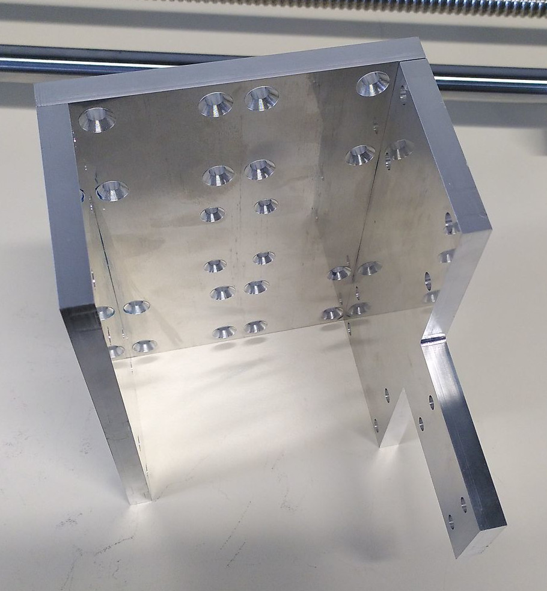
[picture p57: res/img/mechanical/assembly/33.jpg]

<figcaption> Figure 11.2: Assembled carriage for the z-axis (plate 5, 6 and 7). </figcaption>

---

11.3 Attach the assembled carriage to the linear bearings of the z-axis Easy-Mechatronics System using the _Screws, M6x20, countersunk_. _Aluminum Plate 5_ should be pointing towards the motor holder.

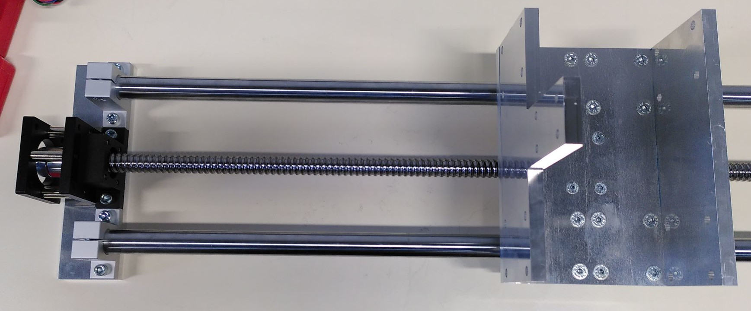
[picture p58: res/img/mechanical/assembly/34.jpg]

<figcaption> Figure 11.3: Carriage for the z-axis attached to the linear bearings. </figcaption>

---

11.4 Fix _Aluminum Plate 6_ to the ballscrew block using the _Screws M5x20, countersunk_.

#### Step 12

Now we will add the linear rails for the x axis.

| Quantity | Part description               | BoM Number | Comment |
|----------|--------------------------------|------------|---------|
| 2        | Supported rail                 | 9          |         |
| 4        | Linear bearing                 | 11         |         |
| 12       | Screws, M5x30                  | 19         |         |
| 12       | Hexagon nuts, M5               | 21         |         |

12.1 Slide the _Linear bearing_ into the _Supported rail_ (2x top, 2x bottom).

12.2 Place one supportin rail on top of _Aluminum Plate 1_ and put all 12 screws through the holes. Now place the other supporting rail on the bottom, so that the screws go through the holes of the supporting rail. Tighten the screws with the _Hexagon nuts, M5_.


<figcaption> Figure 12.2: Linear rails attached to the x-axis. </figcaption>

---

#### Step 13

Now the z-carriage will be attached to the x-axis.

| Quantity | Part description               | BoM Number | Comment |
|----------|--------------------------------|------------|---------|
| 1        | Assembly of z-carriage         |          | See step 11 |
| 16        | Screws, M6x20     | 18         |         |
| 4        | Screws, M5x20     | 20         |         |
| 4        | Distance Plates 1mm  | 22         |      optional   |

13.1 Attach the z-carriage to the x-axis using the _Screws, M6x20_. You might need to loosen the screws of the z-carriage to slide it onto the x-axis. It might be easier to start with the two top bearings first. If there is a gap between the z-carriage and the bearings, you can use the _Distance Plates 1mm_ to fill the gap.


<figcaption> Figure 13.1: Z-carriage attached to the x-axis. A distance plate was added to the top and the bottom to fill the gap. </figcaption>

---

13.2 Attach _Aluminum Plate 5_ to the z-carriage using the _Screws, M5x20_.


<figcaption> Figure 13.2: Aluminum Plate 5 attached to the z-carriage. </figcaption>

---

#### Step 14

Now we will connect the x-axis and the y-axis.

| Quantity | Part description               | BoM Number | Comment |
|----------|--------------------------------|------------|---------|
| 1        | Aluminum Plate 2       |    6      | See [Technical Drawing](../src/mechanical/Aluplates/FreeCAD/Technical%20Drawings/2018-08-02_COSImeasure_mechanical_plate2.pdf) |
| 4       | Screws, M5x30     | 19         |         |
| 4      | Screws, M5x20     | 18         |         |
| 1 | Distance Plate 1mm | 23 | optional |

---

14.1 Attach _Aluminum Plate 2_ to the x-axis using the _Screws, M5x30_.

14.2 Attach _Aluminum Plate 2_ to the y-axis using the _Screws, M5x20_. You might need to loosen the screws of the y-axis. If there is a gap between the y-axis and the _Aluminum Plate 2_, you can use the _Distance Plate 1mm_ to fill the gap.


<figcaption> Figure 14.2: Aluminum Plate 2 attached to the y-axis. </figcaption>

---

14.3 **Important** You can now tighten the screws of the linear bearings of the y-axis (Step 7.2).

#### Finished

This concludes the basic mechanical assembly. The system should now look like this:


<figcaption> Figure 14.3: Finished mechanical assembly. You might not have the electronics cabinet mounting in case you skipped the optional step. </figcaption>

---

#### TODO

##### Motor Mounting

##### Sensor Mounting

##### Offset Plate

##### Cable Chains

##### Wheels

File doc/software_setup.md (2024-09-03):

# Software Getting Started

<!-- TOC -->

- [Software Getting Started](#software-getting-started)
  - [Installation](#installation)
    - [Download and Install Klipper](#download-and-install-klipper)
    - [Setting things up!](#setting-things-up)
    - [Config File](#config-file)
    - [Going into Bootloader Mode](#going-into-bootloader-mode)
    - [Flashing MCU and getting new Serial Port](#flashing-mcu-and-getting-new-serial-port)
  - [GUI](#gui)
  - [Commandline Interface](#commandline-interface)

<!-- /TOC -->

COSY Measure is using the open source 3D-printer firmware [klipper](https://www.klipper3d.org/). This document leads you through the installation. It´s assumed you have already installed [Raspberry-Pi-OS](https://www.raspberrypi.com/software/). We recommend the latest 64-bit Desktop version.

## Installation

This Quick-Start-Guide is a short summary of <https://www.klipper3d.org/Installation.html> with some modifications for Rumba32 boards.

### 1. Download and Install Klipper

     git clone https://github.com/Klipper3d/klipper
     ./klipper/scripts/install-octopi.sh

Go to [flash-mcu.sh](../src/software/flash-mcu.sh) and change the path in line 19 to the path of the repository above. For me line 19 is

     19:  cd /home/cosi/klipper

### 2.1 Setting things up

     cd klipper
     make menuconfig 

Opens a menu. Set

- Enable extra low-level configuration options
- Micro-controller Architecture (STMicroelectronics STM32)
- Processor model (STM32F446)
- Bootloader offset (32KiB bootloader)
- Clock Reference (12 MHz crystal)
- Communication interface (USB (on PA11/PA12))
- USB ids (doesnt matter. But choose something)
- no GPIO pins to set at startup ()

### 2.2 Config File

Get or write a ```printer.cfg```-file, here is mine: [printer.cfg](../src/software/printer.cfg)

Save it as a file named "printer.cfg" in the home directory of the pi user (i.e. ```/home/cosi/printer.cfg```).

This file contains all machine configurations. Further reading: <https://www.klipper3d.org/Installation.html#obtain-a-klipper-configuration-file>

### 3. Going into Bootloader Mode

If not already done, install ```pigpio```for controlling the GPIO pins via the comand line:

     sudo apt-get install pigpio
     sudo systemctl enable pigpiod
     sudo systemctl start pigpiod

The shell script ```flash-mcu.sh``` will set the Rumba board into bootloader mode and eventually will try to flash the MCU. Execute

     ./flash-mcu.sh

to set the board into bootloader mode. Because it doesn´t know yet the usb-id of the microcontroller it will fail to flash - ignore that for now. Search the Device ID by executing

     lsusb

This will show up something like

     Bus 002 Device 001: ID 1d6b:0003 Linux Foundation 3.0 root hub
     Bus 001 Device 031: ID 0483:df11 STMicroelectronics STM Device in DFU Mode
     Bus 001 Device 002: ID 2109:3431 VIA Labs, Inc. Hub

So in my installation ```0483:df11``` is the ID of the STM-chip of Rumba32. Change line 20 in ```flash-mcu.sh``` to your device ID and save the file.

### 4. Flashing MCU and getting new Serial Port

Execute ```flash-mcu.sh``` again. Now it should flash the MCU. This will eventually look something like

     Downloading to address = 0x08008000, size = 29236
     Download [=========================] 100%        29236 bytes
     Download done.
     File downloaded successfully
     Transitioning to dfuMANIFEST state
     dfu-util: can't detach
     Resetting USB to switch back to runtime mode
     cosi@raspberrypi:~/klipper $ 

Then search for serial ports by executing

     ls /dev/serial/by-id/*

this will return something similar to

     /dev/serial/by-id/usb-Klipper_stm32f446xx_280058000951363131343032-if00

Copy and paste it in ```/home/cosi/printer.cfg``` to your MCU serial definition:

     [mcu]
     serial: /dev/serial/by-id/usb-Klipper_stm32f446xx_280058000951363131343032-if00

Congratulations, now you´re done. Get a coffee. Enjoy.

## GUI

A GUI was developed in Python for COSI measure. You can install all required packages (ideally in a virtual environment) by running:

```bash
pip install -r requirements.txt
```

To start the GUI, run:

```bash
python main.py
```

## Commandline Interface

Start the klipper service with executing

     sudo service klipper start

Klipper can be controlled via the following virtual serial port:

     /tmp/printer

Use 250000 Baud for communication. You can send G-code to this serial port and receive status information of the machine, refer to <https://www.klipper3d.org/G-Codes.html>.

There are some custom g-code macros for disabling and enabling the drives without letting klipper loose it´s homing, for details see [printer.cfg](../src/software/printer.cfg) and [driver breakoutboard](../doc/rumba32/driver_breakoutboard_assembly.md). Use this commands only at standstill and never run a movement with disabled drives as this would eventually lead to false positioning.

Stop the klipper service by executing

     sudo service klipper stop

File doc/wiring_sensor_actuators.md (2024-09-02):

# Wiring sensors and actuators

<!--For cable selection keep in mind, that most cables must be for moving cable chain applications. Use shielded cables for the motors.-->

## Cable Chains
We have a total of three cable chains.

## Motors

### Motor Housing

For wiring the stepper motors you first want to 3D print the motor housings and then add the GX20 connectors. The STL file can be found [here]().

### Motor Cable

## Sensors

### Sensor Box

### Inductive Proximity Sensors

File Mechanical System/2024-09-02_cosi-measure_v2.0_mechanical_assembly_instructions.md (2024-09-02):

# COSI Measure Assembly

The repository containing the COSI measure design files, BOM and assembly instructions can be found [here](https://github.com/opensourceimaging/cosi-measure)

The commit this document is based on is `6160283cf2638d430e5380868da4b0e1bf4a42c2` and the branch is `main`.
Careful with links in this document, I'm using permalinks so they might be outdated.

## Table of Contents

1. [Introduction](#introduction)
2. [Ordering Parts and Build Notes](#ordering-parts-and-build-notes)
3. [Assembly](#assembly)
    1. [Mechanical Assembly](#mechanical-assembly)
    2. [Electrical Assembly](#electrical-assembly)
4. [Testing](#testing)

## Introduction

We have two different assemblies to do, the mechanical assembly and the electrical assembly. The mechanical assembly is straightforward - just follow the assembly instructions.

For the electrical part some PCBs have to be manufactured and you should probably have some experience with wiring electronics.

## Ordering Parts and Build Notes

The BOM for the mechanical parts can be found [here](https://github.com/opensourceimaging/cosi-measure/blob/223aed325aeb5dffe3ebcb21c4bbc3dcf3c00471/Mechanical%20System/2018-08-24_cosi-measure_v1.0_BoM_mechanical.ods). You need to manufacture some parts, like the aluminum plates, and order some parts, like the linear bearings.

Technical drawings for the aluminum plates can be found [here](https://github.com/opensourceimaging/cosi-measure/tree/6160283cf2638d430e5380868da4b0e1bf4a42c2/Mechanical%20System/Aluplates/FreeCAD/Technical%20Drawings).

The links in the BOM are still valid, so you can use them to order the parts (April-2024).

Make sure to order a few extra screws and nuts, since you don't want to be stuck in the middle of the assembly process because you are missing a screw.

The final assembly is quite large, so make sure you can still transport it to the place where you want to use it.

## Assembly

### Mechanical Assembly

#### Step 1

| Quantity | Part description              | BoM Number | Comment |
|----------|-------------------------------|------------|---------|
| 6        | Aluminum Frames (40x80x800)mm | 1          |         |
| 8        | Angles, 40x80                 | 2          |         |
| 36       | Slot nuts, M8                 | 2/4        |         |
| 32       | Screws, M8x18                 | 2          |         |


<figcaption>Figure 1: Components needed for step 1. Two aluminum profiles are missing in the picture. </figcaption>

---

1.1. Insert the _Slot nuts, M8_ into the _Aluminum Frames (40x80x800)mm_.


<figcaption>Figure 1.1: Inserted slots for two of the aluminum frames. Do this for all 6 parts.    </figcaption>

---

1.2 Add _Angles, 40x80_ to two of the _Aluminum Frames (40x80x800)mm_ using the _Screws, M8x18_ and the previously inserted _Slot nuts, M8_. I placed the _Angles, 40x80_ with the bridge facing each other to avoid forming a hard to clean cavity.


<figcaption> Figure 1.2: Aluminium frames with the the angles mounted.</figcaption>

---

1.3 Take four _Slot nuts, M8_ and insert them into the _Aluminum Frames (40x80x800)mm_ with the mounted angles. Do this on the short side, perpendicular to where you placed the slot nuts in the aluminum frames previously.


<figcaption> Figure 1.3: Slot nuts inserted into the angles. </figcaption>

---

1.4 Form a U shape with the frame with the angle mounted and two of the frames without angles. Do this twice to obtain two U shapes.


<figcaption> Figure 1.4: U shape formed with the frames. </figcaption>

---

#### Step 2

| Quantity | Part description              | BoM Number | Comment |
|----------|-------------------------------|------------|---------|
| 2        | Aluminum Frames (40x40x800)mm | 3          |         |
| 8        | Angles, 40x40                 | 4          |         |
| 12       | Slot nuts, M8                 | 4          |         |
| 16       | Screws, M8x16, countersunk    | 4          |         |


<figcaption> Figure 2: Components needed for step 2. </figcaption>

---

2.1 Add two _Slot nuts, M8_ to the _Aluminum Frames (40x40x800)mm_ in a perpendicular fashion.


<figcaption> Figure 2.1: Slot nuts inserted into the aluminum frame. Do this for both sides for both aluminum frames. </figcaption>

---

2.2 Connect the _Aluminum Frames (40x40x800)mm_ with the _Angles, 40x40_ using the _Screws, M8x16, countersunk_. Then use the _Aluminum Frames (40x40x800)mm_ with the _Angles, 40x40_ attached, to connect the U shapes from step 1.


<figcaption> Figure 2.2: Aluminum frames connected with the angles. </figcaption>

#### Step 3

| Quantity | Part description | BoM Number | Comment |
|----------|------------------|------------|---------|
| 18       | Slot nuts, M8    | 4          |         |

---

3.1 Add the _Slot nuts, M8_ to the top of the upright standing aluminum frames (inner side).

#### Step 4

| Quantity | Part description               | BoM Number | Comment |
|----------|--------------------------------|------------|---------|
| 18       | Slot nuts, M8                  | 4          |         |
| 2        | Aluminum frames, (40x80x880)mm | 5          |         |
| 8        | Angles, 40x80                  | 2          |         |
| 32       | Screws, M8x18                  | 2          |         |

<figcaption> Figure 4: Components needed for step 4. </figcaption>

---

4.1 We add the _Slot nuts, M8_ to the _Aluminum frames, (40x80x880)mm_. Four on each side on the long side. On the short (perpendicular) side we add two _Slot nuts, M8_.

4.2 Attach the _Angles, 40x80_ to the _Aluminum frames, (40x80x880)mm_ using the _Screws, M8x18_.


<figcaption> Figure 4.2: Angles attached to the aluminum frames. </figcaption>

---

4.3 Attach the _Angles, 40x80_ to the U shapes from step 2 using the _Screws, M8x18_.

<figcaption> Figure 4.3: U shapes connected to the aluminum frames. </figcaption>

---

#### Step 5

| Quantity | Part description               | BoM Number | Comment |
|----------|--------------------------------|------------|---------|
| 1        | Aluminum frame, (40x40x800)mm | 3          |         |
| 8        | Screws, M8x16, countersunk     | 4          |         |
| 4        | Slot nuts, M8                  | 4          |         |
| 4        | Angles, 40x40                  | 4          |         |

<figcaption> Figure 5: Components needed for step 5. </figcaption>

---

5.1 Add the _Slot nuts, M8_ to the _Aluminum frame, (40x40x800)mm_ similar to Figure 2.1.

5.2 Use the angles to connect the _Aluminum frame, (40x40x800)mm_ to backside of the assembled structure.


<figcaption> Figure 5.2: Aluminum frame (40x40x800)mm attached to the backside of the structure. </figcaption>

---

##### Optional Step

If you want to attach the electronics cabinet to the aluminum frame, you can add two additional _Aluminum frames, (40x40x800)mm_ to the left side of the structure. Make sure to have a distance between the two aluminum profiles that is equal to the mounting holes of the electronics cabinet.

| Quantity | Part description               | BoM Number | Comment |
|----------|--------------------------------|------------|---------|
| 8        | Slot nuts, M8                  | (optional) |         |
| 2        | Aluminum frame, (40x40x800)mm  | (optional) |         |
| 8        | Screws, M8x16, countersunk     | (optional) |         |

---


<figcaption> Figure 5.3: Aluminum frame (40x40x800)mm attached to the left side of the structure for mounting of the electronics cabinet. </figcaption>

---

You might want to loosen the upper screws of the aluminum frame to slide the aluminum profiles in.

You can also flip the structure to the side and place the electronics cabinet on th the aluminum profiles the check if the mounting holes align.

If you want the final assembly to be a little less broad, you can also add the _Aluminum frames, (40x40x800)mm_ to the inner side of the structures _Aluminum frames, (40x80x800)mm_.

---

#### Step 6

Now we will attach the plates for the y-axis motor and spindle. Note: the pictures are without the optional step.

| Quantity | Part description               | BoM Number | Comment |
|----------|--------------------------------|------------|---------|
| 10       | Slot nuts, M8                  | 5          |         |
| 1        | Aluminum plate 3               | 6          | See [Technical Drawing](https://github.com/opensourceimaging/cosi-measure/blob/6160283cf2638d430e5380868da4b0e1bf4a42c2/Mechanical%20System/Aluplates/FreeCAD/Technical%20Drawings/2018-08-02_COSImeasure_mechanical_plate3.pdf)         |
| 1        | Aluminum plate 4               | 6          | See [Technical Drawing](https://github.com/opensourceimaging/cosi-measure/blob/6160283cf2638d430e5380868da4b0e1bf4a42c2/Mechanical%20System/Aluplates/FreeCAD/Technical%20Drawings/2018-08-02_COSImeasure_mechanical_plate4.pdf)         |
| 10         | Screws, M8x20, countersunk  | 7          |         |

---

6.1 Insert the 6 _Slot nuts, M8_ into the aluminum frame on the "left back side" of the structure.

6.2 Insert the 4 _Slot nuts, M8_ into the aluminum frame on the "right side" of the structure.

---


<figcaption> Figure 6: The Slot nuts, M8 that have been added to the aluminum frames are marked in red. </figcaption>

---

6.3 Attach the _Aluminum plate 3_ to the aluminum frame on the "left back side" of the structure using the _Screws, M8x20, countersunk_.


<figcaption> Figure 6.3: Aluminum plate 3 attached to the aluminum frame. </figcaption>

---

6.4 Attach the _Aluminum plate 4_ to the aluminum frame on the "right side" of the structure using the _Screws, M8x20, countersunk_.


<figcaption> Figure 6.4: Aluminum plate 4 attached to the aluminum frame. </figcaption>

---

#### Step 7

| Quantity | Part description               | BoM Number | Comment |
|----------|--------------------------------|------------|---------|
| 24       | Slot nuts, M5                  | 8          |         |
| 2        | Supported rail, TBS20          | 9          |         |
| 24       | Screws, M5x20                  | 10         |         |
|4         | Linear bearing, TBR20UU        | 11         |         |

<figcaption> Figure 7.2: Components needed for step 7 </figcaption>

---

7.1 Insert the _Slot nuts, M5_ into top aluminum frame (24 in total).

7.2 Attach the _Supported rail, TBS20_ to the top aluminum frame using the _Screws, M5x20_. **Don't tighten the screws yet.**

7.3 Slide the _Linear bearing, TBR20UU_ into the _Supported rail, TBS20_.


<figcaption> Figure 7.3: Supported rail attached to the top aluminum frame. </figcaption>

---

#### Step 8

Now the spindle block with the motor holder will be assembled for the x and y-axis (Easy-Mechatronics System).

| Quantity | Part description               | BoM Number | Comment |
|----------|--------------------------------|------------|---------|
| 2        | Ballscrew & spindle nut block  | 12         |         |
| 2        | Fixed bearing & motor holder   | 13         |         |
| 2        | Floating bearing               | 14         |         |
| 2        | Motor coupler                  | 15         |         |


<figcaption> Figure 8: Components needed for step 8. These are only for one of the axes, so you will need all components twice. You will need some additional screws for assembly of the spindle block.</figcaption>

---

8.1 You can find assembly instructions for the assembly of the Easy-Mechatronics system block in [this video](https://invidious.private.coffee/watch?v=Gt8ER-_8GjY). The spindle block itself needs to be assembled differently in comparison to the video. Instructions for the spindle block assembly can be found [here](https://invidious.private.coffee/watch?v=TItAG3wGPzI).
The grease fitting should be on the upper side of the spindle block for one of the axes and on the lower side for the other axis. This makes sure the grease fitting is accessible after the assembly of the complete system.


<figcaption> Figure 8.1: Assembled Easy-Mechatronics System for the x and y axis. </figcaption>

---

#### Step 9

Now we will build the z-axis.

| Quantity | Part description               | BoM Number | Comment |
|----------|--------------------------------|------------|---------|
| 1        | Easy-Mechatronics System       | 16         |         |
| 1        | Aluminum plate 8               | 6          | See [Technical Drawing](https://github.com/opensourceimaging/cosi-measure/blob/6160283cf2638d430e5380868da4b0e1bf4a42c2/Mechanical%20System/Aluplates/FreeCAD/Technical%20Drawings/2018-08-02_COSImeasure_mechanical_plate8.pdf) |
| 1        | Aluminum plate 9               | 6          | See [Technical Drawing](https://github.com/opensourceimaging/cosi-measure/blob/6160283cf2638d430e5380868da4b0e1bf4a42c2/Mechanical%20System/Aluplates/FreeCAD/Technical%20Drawings/2018-10-11_COSImeasure_mechanical_plate9.pdf) |
| 12      | Screws, M6x20               | 17          |         |

---

9.1 Assemble the Easy-Mechatronics System for the z-axis just as you did for the x and y-axis. Make sure the grease fitting is accessible after the assembly of the complete system.

9.2 Attach the _Aluminum plate 8_ and _Aluminum plate 9_  to the Easy-Mechatronics System for the z-axis using the _Screws, M6x20_. Make sure you have the correct orientation: The motor holder is on the smaller _Aluminum plate 8_.


<figcaption> Figure 9.2: Assembled Easy-Mechatronics System for the z-axis. </figcaption>

---

#### Step 10

Now we will attach the x and y-axis to the structure.

| Quantity | Part description               | BoM Number | Comment |
|----------|--------------------------------|------------|---------|
| 1        | Aluminum Plate 1               | 6          | See [Technical Drawing](https://github.com/opensourceimaging/cosi-measure/blob/6160283cf2638d430e5380868da4b0e1bf4a42c2/Mechanical%20System/Aluplates/FreeCAD/Technical%20Drawings/2018-08-02_COSImeasure_mechanical_plate1_1of2.pdf)
| 16       | Screws, M6x20, countersunk    | 18         |         |
| 2        | Assembly of x and y-axis      |          | See step 8|

| 6        | Screws, M6x20                 | 17         |         |
| 2        | Screws, M6x30                 | 24         |         |
| 2        | Screw nuts, M6                | 25         |         |

---

10.1 Attach the _Aluminum Plate 1_ to four linear bearings using the _Screws, M6x20, countersunk_.


<figcaption> Figure 10.1: Aluminum Plate 1 attached to the linear bearings. </figcaption>

---

10.2 Attach the x-axis to _Aluminum Plate 1_ using the _Screws, M6x20_. Make sure to orient the motor correctly. It makes sense to have the motor on the side of the electronics cabinet. You don't need to mount the motor yet.

<p float="left">
  
  
</p>

---

10.3 Attach the y-axis to the _Aluminum Plate 3_ using the _Screws, M6x30_ together with the _Screw nuts, M6_ (motor side). Attach the other side of the y-axis to the _Aluminum Plate 4_ using the _Screws, M6x20_.

<p float="left">
  
  
</p>

---

#### Step 11

We now assemble the carriage for the z-axis.

| Quantity | Part description               | BoM Number | Comment |
|----------|--------------------------------|------------|---------|
| 1        | Aluminum Plate 5               | 6          | See [Technical Drawing](https://github.com/opensourceimaging/cosi-measure/blob/6160283cf2638d430e5380868da4b0e1bf4a42c2/Mechanical%20System/Aluplates/FreeCAD/Technical%20Drawings/2018-08-02_COSImeasure_mechanical_plate5.pdf) |
| 1        | Aluminum Plate 6               | 6          | See [Technical Drawing](https://github.com/opensourceimaging/cosi-measure/blob/6160283cf2638d430e5380868da4b0e1bf4a42c2/Mechanical%20System/Aluplates/FreeCAD/Technical%20Drawings/2018-08-02_COSImeasure_mechanical_plate6.pdf) |
| 1        | Aluminum Plate 7               | 6          | See [Technical Drawing](https://github.com/opensourceimaging/cosi-measure/blob/6160283cf2638d430e5380868da4b0e1bf4a42c2/Mechanical%20System/Aluplates/FreeCAD/Technical%20Drawings/2018-08-02_COSImeasure_mechanical_plate7.pdf) |
| 4       | Screws, M5x30                 | 19         |         |
| 16      | Screws, M6x20, countersunk    | 18         |         |
| 4       | Screws, M5x30, countersunk    | 24         |         |


<figcaption> Figure 11: Components needed for step 11. </figcaption>

---

11.1 Connect _Aluminum Plate 5_ to _Aluminum Plate 6_ using the _Screws, M5x30_.

11.2 Connect _Aluminum Plate 6_ to _Aluminum Plate 7_ using the _Screws, M6x30. The assembly should look like this:


<figcaption> Figure 11.2: Assembled carriage for the z-axis (plate 5, 6 and 7). </figcaption>

---

11.3 Attach the assembled carriage to the linear bearings of the z-axis Easy-Mechatronics System using the _Screws, M6x20, countersunk_. _Aluminum Plate 5_ should be pointing towards the motor holder.


<figcaption> Figure 11.3: Carriage for the z-axis attached to the linear bearings. </figcaption>

---

11.4 Fix _Aluminum Plate 6_ to the ballscrew block using the _Screws M5x20, countersunk_.

#### Step 12

Now we will add the linear rails for the x axis.

| Quantity | Part description               | BoM Number | Comment |
|----------|--------------------------------|------------|---------|
| 2        | Supported rail                 | 9          |         |
| 4        | Linear bearing                 | 11         |         |
| 12       | Screws, M5x30                  | 19         |         |
| 12       | Hexagon nuts, M5               | 21         |         |

12.1 Slide the _Linear bearing_ into the _Supported rail_ (2x top, 2x bottom).

12.2 Place one supportin rail on top of _Aluminum Plate 1_ and put all 12 screws through the holes. Now place the other supporting rail on the bottom, so that the screws go through the holes of the supporting rail. Tighten the screws with the _Hexagon nuts, M5_.


<figcaption> Figure 12.2: Linear rails attached to the x-axis. </figcaption>

---

#### Step 13

Now the z-carriage will be attached to the x-axis.

| Quantity | Part description               | BoM Number | Comment |
|----------|--------------------------------|------------|---------|
| 1        | Assembly of z-carriage         |          | See step 11 |
| 16        | Screws, M6x20     | 18         |         |
| 4        | Screws, M5x20     | 20         |         |
| 4        | Distance Plates 1mm  | 22         |      optional   |

13.1 Attach the z-carriage to the x-axis using the _Screws, M6x20_. You might need to loosen the screws of the z-carriage to slide it onto the x-axis. It might be easier to start with the two top bearings first. If there is a gap between the z-carriage and the bearings, you can use the _Distance Plates 1mm_ to fill the gap.


<figcaption> Figure 13.1: Z-carriage attached to the x-axis. A distance plate was added to the top and the bottom to fill the gap. </figcaption>

---

13.2 Attach _Aluminum Plate 5_ to the z-carriage using the _Screws, M5x20_.


<figcaption> Figure 13.2: Aluminum Plate 5 attached to the z-carriage. </figcaption>

---

#### Step 14

Now we will connect the x-axis and the y-axis.

| Quantity | Part description               | BoM Number | Comment |
|----------|--------------------------------|------------|---------|
| 1        | Aluminum Plate 2       |    6      | See [Technical Drawing](https://github.com/opensourceimaging/cosi-measure/blob/6160283cf2638d430e5380868da4b0e1bf4a42c2/Mechanical%20System/Aluplates/FreeCAD/Technical%20Drawings/2018-08-02_COSImeasure_mechanical_plate2.pdf) |
| 4       | Screws, M5x30     | 19         |         |
| 4      | Screws, M5x20     | 18         |         |
| 1 | Distance Plate 1mm | 23 | optional |

---

14.1 Attach _Aluminum Plate 2_ to the x-axis using the _Screws, M5x30_.

14.2 Attach _Aluminum Plate 2_ to the y-axis using the _Screws, M5x20_. You might need to loosen the screws of the y-axis. If there is a gap between the y-axis and the _Aluminum Plate 2_, you can use the _Distance Plate 1mm_ to fill the gap.


<figcaption> Figure 14.2: Aluminum Plate 2 attached to the y-axis. </figcaption>

---

14.3 **Important** You can now tighten the screws of the linear bearings of the y-axis (Step 7.2).

#### Finished

This concludes the basic mechanical assembly. The system should now look like this:


<figcaption> Figure 14.3: Finished mechanical assembly. You might not have the electronics cabinet mounting in case you skipped the optional step. </figcaption>

---

#### TODO

##### Motor Mounting

##### Sensor Mounting

##### Offset Plate

##### Cable Chains

##### Wheels

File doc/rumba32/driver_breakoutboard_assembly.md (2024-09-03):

# Driver Breakout Board

<!-- TOC -->

- [Driver Breakout Board](#driver-breakout-board)
  - [Enable Logic](#enable-logic)
  - [Schematic](#schematic)
  - [BOM](#bom)
  - [Setting jumpers on Rumba32](#setting-jumpers-on-rumba32)
    - [STEPPER_DRIVER_LOGIC JUMPER](#stepper_driver_logic-jumper)
    - [Additional Software Enable Jumpers](#additional-software-enable-jumpers)

<!-- /TOC -->

Breakout Board

This breakoutboard can be placed to the motor driver slots into the Rumba32 board.
It is useful for wiring the step, direction and enable pins via the motor connector to external motor drivers. In addition it supports an easy way of integrating a drive-enable functionality.

## Enable Logic

There can be current on the drives, if

- The Firmware enables the drives and
- some control pins are low (further explanation below) and
- Emergency Stop Relais provides it's NPN-ok signal ($0 \ V$).
- Contactor -Q1 is closed (no safe-torque-off)

Many 3D-printing firmwares are not designed for switching off the drives completely while executing a G-code file. But COSI-Measure is meant to perform magnetic measurements, so it must not disturb the measurements with noisy motor currents while performing a measurement.

A convenient workaround for Klipper is to switch on and off some extra GPIO Pins, that are wired to the hardware-enable-logic. In case you are doing something different and you do not need this feature, feel free to ignore it. Default of these Pins is low, which is also the enabled state. For details about it see the [printer.cfg](../../src/software/printer.cfg) file line 275-317. The drives can be enabled and disabled with g-code macros while keeping the homing active.

The NPN-ok-signal from the emergency stop relais can be daisy-chained with standard 2.54 mm jumpers to the next breakout board.

The enable input of the motordriver is not meant for a safe-torque-off function (emergency stop). Safe-torque-off is implemented in hardware (mechanical relais, contactors etc.), see [schematics](../enclosure_wiring.md#emergencystop).
Anyway, to prevent driver malfunction the driver will be disabled with semiconductor only circuits before the power supply of the driver will be disconnected. The delay is coming from the slower reaction of mechanical contactors and relays, so no dedicated timing module is needed.

## Schematic

Schematic

## BOM

This Bill-of-Materials is for 1 breakout board only. You need one breakout board for each motor with external motor drivers, usually 3 in total (depending to your setup).

| #  | Designator | Quantity | Comment              | Man. Part-No       | Link                                                                                            |
|----|------------|----------|----------------------|--------------------|-------------------------------------------------------------------------------------------------|
| 1  | C1         | 1        | 10 nF, 0805          | C0805C103K2RECAUTO | <https://www.digikey.de/de/products/detail/kemet/C0805C103K2RECAUTO/8646745>                    |
| 2  | D1         | 1        | Dual LED red/green   | AAA3528ESGCT       | <https://www.digikey.de/de/products/detail/kingbright/AAA3528ESGCT/7318936>                     |
| 3  | IC1        | 1        | OR-Gate              | SN74ACT32PWR       | <https://www.digikey.de/en/products/detail/texas-instruments/SN74ACT32PWR/376063>               |
| 4  | J1, J2     | 2        | 8 pin header 2.54    | 61300811121        | <https://www.digikey.de/de/products/detail/w%C3%BCrth-elektronik/61300811121/4846839>           |
| 5  | J3, J5     | 2        | 2 pin header 2.54    | 61300211121        | <https://www.digikey.de/de/products/detail/w%C3%BCrth-elektronik/61300211121/4846823>           |
| 6  | J4         | 1        | 2 pos screw terminal | 0393570002         | <https://www.digikey.de/de/products/detail/molex/0393570002/946543>                             |
| 7  | Q1         | 1        | NPN Transistor       | MMBT3904           | <https://www.digikey.de/de/products/detail/micro-commercial-co/MMBT3904-TP/717280>              |
| 8  | R1         | 1        | 47 kOhm, 0805        | WR08X473 JTL       | <https://www.digikey.de/de/products/detail/walsin-technology-corporation/WR08X473-JTL/13240617> |
| 9  | R2         | 1        | 270 Ohm, 0805        | RMCF0805JT270R     | <https://www.digikey.de/de/products/detail/stackpole-electronics-inc/RMCF0805JT270R/1757887>    |
| 10  | R3, R5    | 2        | 200 Ohm, 0805        | RMCF0805FT200R     | <https://www.digikey.de/de/products/detail/stackpole-electronics-inc/RMCF0805FT200R/1760343>    |
| 11 | R4         | 1        | 1.2 kOhm, 0805       | RMCF0805JT1K20     | <https://www.digikey.de/de/products/detail/stackpole-electronics-inc/RMCF0805JT1K20/1757811>    |
| 12 | -          | 3        | 2.54 mm jumper       | QPC02SXGN-RC       | <https://www.digikey.de/en/products/detail/sullins-connector-solutions/QPC02SXGN-RC/2618262>    |

## Setting jumpers on Rumba32

### STEPPER_DRIVER_LOGIC JUMPER

The STEPPER_DRIVER_LOGIC jumper (see picture below) selects the logic voltage supplied to all stepper driver
sockets. By default, it is configured so that 3.3V is supplied to the stepper drivers. However, since the external motor drivers need 5 V, the track between the centre and 3V pad should be cut, and a solder joint placed over the 5V and centre pad. <br>
voltage selection <br>
(picture and parts of the text above borrowed from <https://github.com/Aus3D/RUMBA32/blob/master/Resources/Manual/RUMBA32%20V1.1%20User%20Manual%20-%20REV%20A.pdf>, License: GPLv2)

### Additional Software Enable Jumpers

Set the jumpers beneath the breakoutboards as seen in the picture below (blue):

jumper placement <br>
(Picture borrowed and modified from <https://github.com/Aus3D/RUMBA32?tab=readme-ov-file>, License: GPLv2)

These jumpers are connecting some GPIO-Pins to the enable logic of this breakout board.

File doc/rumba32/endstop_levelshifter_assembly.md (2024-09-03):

# Endstop BreakoutBoard

Breakout Board

This breakoutboard needs to be placed into Rumba32 Endstop connector. It is a levelshifter for the 12 V Endstops.

12V is supplied by Rumba32, you need to connect the 12V Pins of Rumba32 to J4 of this breakout board.

## Schematic

Schematic

## BOM

| ld  | Designator  | Quantity  | Comment            | Manufacturer Part No  | Link Digikey                                                                           |
|---- |------------ |---------- |------------------- |---------------------- |--------------------------------------------------------------------------------------- |
| 1   | J1          | 1         | Screw Terminal     | 691210910008          | <https://www.digikey.de/de/products/detail/w%C3%BCrth-elektronik/691210910008/11478428>  |
| 2   | C1          | 1         | 10n                | C0805C103K2RECAUTO    | <https://www.digikey.de/de/products/detail/kemet/C0805C103K2RECAUTO/8646745>             |
| 3   | J4          | 1         | 2 Pin Header 2.54  | 0022289020            | <https://www.digikey.de/de/products/detail/molex/0022289020/3158803>                     |
| 4   | J3          | 1         | 3 Pin Header 2.54  | 801-87-003-10-001101 | <https://www.digikey.de/de/products/detail/preci-dip/801-87-003-10-001101/3757430>       |
| 5   | J2          | 1         | 5 Pin Header 2.54  | 801-87-005-10-001101  | <https://www.digikey.de/de/products/detail/preci-dip/801-87-005-10-001101/3757433>       |
| 6   | IC1         | 1         | Buffer             | 74HC4050PW,118        | <https://www.digikey.de/de/products/detail/nexperia-usa-inc/74HC4050PW-118/1230398>      |

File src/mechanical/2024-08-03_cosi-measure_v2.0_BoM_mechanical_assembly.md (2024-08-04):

# Mechanical Subsystem Components

| Number | Item | Description | Price | Pcs | Total Price | Links |
|--------|------|------------|-------|-----|-------------|-------|
| 1 | Aluminum frame | 40x80L I-Typ Nut 8, 80cm | 17.2 | 6 | 103.2 | [Link](https://www.dold-mechatronik.de/Aluminiumprofil-40x80L-I-Typ-Nut-8-Standardlaengen-215-EUR-m) |
| 2 | Angle | 40x80 l-Typ Nut 8 + screws | 4.66 | 16 | 74.56 | [Link](https://www.dold-mechatronik.de/Winkel-40x80-I-Typ-Nut-8-inkl-Befestigungssatz) |
| 3 | Aluminum frame | 40x40L I-Typ Nut 8, 80cm | 8.2 | 3 | 24.6 | [Link](https://www.dold-mechatronik.de/Aluminiumprofil-40x40L-I-Typ-Nut-8-Standardlaengen-1025-EUR-m) |
| 4 | Angle | 40 I-Typ Nut 8 + screws | 2.52 | 12 | 30.24 | [Link](https://www.dold-mechatronik.de/Stahlwinkel-40-I-Typ-Nut-8-inkl-Befestigungssatz) |
| 5 | Aluminum frame | 40x80L I-Typ Nut 8, 88cm | 19.66 | 2 | 39.32 | [Link](https://www.dold-mechatronik.de/Aluminiumprofil-40x80L-I-Typ-Nut-8-ZUSCHNITT-bis-1200-mm-2200-EUR-m-030-EUR-pro-Schnitt) |
| 6 | Slot nut | I-Typ Nut8, M8 | 0.53 | 10 | 5.3 | [Link](https://www.dold-mechatronik.de/Nutenstein-mit-Steg-I-Typ-Nut-8-Gewindedurchmesser-waehlbar) |
| 7 | Aluminum plate | AlCuMg1, EN AW-2017A.EN AW-AlCu4MgSi(A), T451 EN 485- 1.2.3 | 184.45 | 1 | 184.45 | [Link](http://www.gemmel-metalle.de) |
| 8 | Screws | DIN7991-M8x20, countersunk | 0.3 | 10 | 3 | [Link](https://www.dold-mechatronik.de/DIN-7991-Senkschraube-mit-Innensechskant-88-verzinkt) |
| 9 | Slot nut | I-Typ Nut8, M5 | 0.53 | 24 | 12.72 | [Link](https://www.dold-mechatronik.de/Nutenstein-mit-Steg-I-Typ-Nut-8-Gewindedurchmesser-waehlbar) |
| 10 | Supported Rail | TBS20 rail 800mm | 33 | 4 | 132 | [Link](https://www.dold-mechatronik.de/Linearfuehrung-Supported-Rail-TBS20-800mm-lang) |
| 11 | Screw | DIN912-M5x20 | 0.13 | 32 | 4.16 | [Link](https://www.dold-mechatronik.de/DIN-912-Zylinderschraube-mit-Innensechskant-88-verzinkt) |
| 12 | Linear bearing | TBR20UU | 9.8 | 8 | 78.4 | [Link](https://www.dold-mechatronik.de/Linearlager-20mm-TBR20UU-offen-Spiel-einstellbar) |
| 13 | Ballscrew + spindle nut block | SFU1605-DM 652mm | 95 | 2 | 190 | [Link](https://www.dold-mechatronik.de/SET-Kugelumlaufspindel-SFU1605-DM-642mm-mit-Spindelmutterblock-fuer-Easy-Mechatronics-System-1620A-L600) |
| 14 | Fixed bearing + motor holder | FLB20-3200 fixed bearing and NEMA23 Motorholder | 53.9 | 2 | 107.8 | [Link](https://www.dold-mechatronik.de/Festlagereinheit-FLB20-3200-inkl-Motorhalter-NEMA23-Easy-Mechatronics-System-1620B) |
| 15 | Floating Bearing | LLB20-6200 floating bearing | 14.9 | 2 | 29.8 | [Link](https://www.dold-mechatronik.de/Loslagereinheit-LLB20-6200-Easy-Mechatronics-System-1620B) |
| 16 | Motor coupler | D25L30 8/8 | 10.5 | 2 | 21 | [Link](https://www.dold-mechatronik.de/Wellenkupplung-XB-flexibel-D25L30-800-800mm) |
| 17 | Easy-Mechatronics System | Linear axis configuration: 1x fixed bearing and motor holder NEMA23, 1x floating bearing, 4x linear bearings SCJ20UU, 2x präzisionshaft 20mm h6 840mm, 4x shaftholder SH20, 1x ballscrew with spindle nut block SFU1605-DM 852mm, 1x shaft| 271.3 | 1 | 271.3 | [Link](https://www.dold-mechatronik.de/Linearachse-Konfigurator-Easy-Mechatronics-System-1620B) , [Link couipling](https://www.dold-mechatronik.de/Wellenkupplung-XB-flexibel-D25L30-800-800mm)|
| 18 | Screw | DIN912-M6x20 | 0.14 | 52 | 7.28 | [Link](https://www.dold-mechatronik.de/DIN-912-Zylinderschraube-mit-Innensechskant-88-verzinkt) |
| 19 | Screw | DIN7991-M6x20, countersunk | 0.3 | 16 | 4.8 | [Link](https://www.dold-mechatronik.de/DIN-7991-Senkschraube-mit-Innensechskant-88-verzinkt-M6x20) |
| 20 | Bolt | DIN912-M5x30 | 0.17 | 20 | 3.4 | [Link](https://www.dold-mechatronik.de/DIN-912-Zylinderschraube-mit-Innensechskant-88-verzinkt) |
| 21 | Screw | DIN7991-M5x20, countersunk | 0.3 | 4 | 1.2 | [Link](https://www.dold-mechatronik.de/DIN-7991-Senkschraube-mit-Innensechskant-88-verzinkt) |
| 22 | Hexagon nut | DIN934-M5 | 0.15 | 24 | 3.6 | [Link](https://www.dold-mechatronik.de/DIN-934-Sechskantmutter-8-verzinkt) |
| 23 | Distance holder | 1mm for TBR20UU linear bearing | 1.5 | 4 | 6 | [Link](https://www.dold-mechatronik.de/Distanzblech-1mm-fuer-TBR20UU) |
| 24 | Distance holder | 1mm for ballscrew block | 1.5 | 2 | 3 | [Link](https://www.dold-mechatronik.de/Distanzblech-1mm-fuer-TR-Muttern-mit-Gehaeuse-16x4-und-16x8-sowie-Spindelmuttergehaeuse-HSFU1605) |

**Total cost mechanical subsystem:**

1341.13

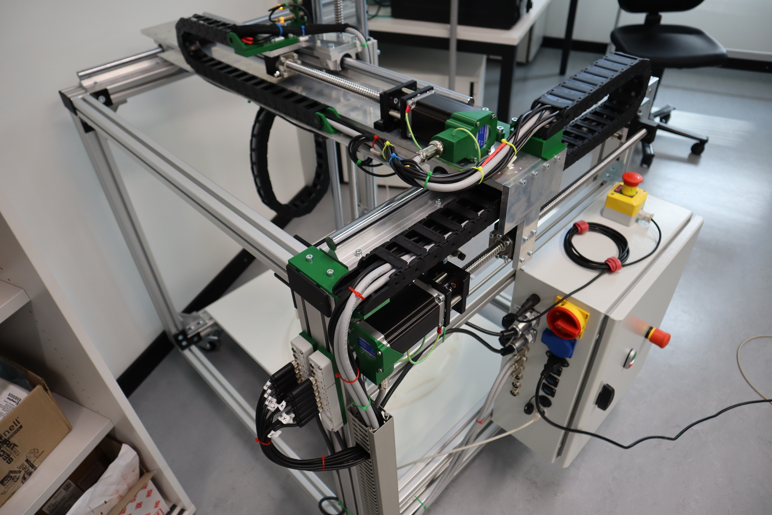
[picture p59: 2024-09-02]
res/img/electrical/sensors_motors/EndstopWiring.JPG

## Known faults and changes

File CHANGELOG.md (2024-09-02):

# Changelog

## Version 2.1

__Hardware:__

- Change to new Safety Relays with direct monitoring of hardware limit switches, updated the schematics accordingly
- Corrected some minor mistakes in the mechanical BoM (e.g. wrong electronics enclosure)
- Added 4C Fuse to the control lines of the stepper motor drivers
- Change to new 5V power supply
- Mounted RUMBA32, Raspberry Pi and DMT542 drivers on DIN rails
- Changed motor connectors to shielded GX20 connectors
- Changed to external sensor boxes for hardware and software limit switches, additionally changed the connectors on the sensors to M12 connectors and the connector to the enclosure to a GX20 connector
- Added 3D printed parts for sensors, cable chains and motor connectors
- Fixed mistake in Breakoutboard layout (Base and Collector of Q1 were swapped)

__Software:__

- Changed installation instructions for the software: Moonraker instead of Octoprint
- Added virtual sensors to printer.cfg
- Added option for Moonraker control to GUI program

__Documentation:__

- Mechanical assembly instructions are now in markdown format
- Updated the electrical assembly instructions for the new hardware

## Version 2.0

- Electronics changed to Rasperry Pi and Rumba32
- Other simplifications e.g. in the power management board
- Up to 6x stepper motor drivers
- Improved safety concept with hardware safe-torque-off and soft and hard limit switches
- New software

## Version 1.0

- Electronics based on Beagle Bone Black and BeBoPr++
- outdated

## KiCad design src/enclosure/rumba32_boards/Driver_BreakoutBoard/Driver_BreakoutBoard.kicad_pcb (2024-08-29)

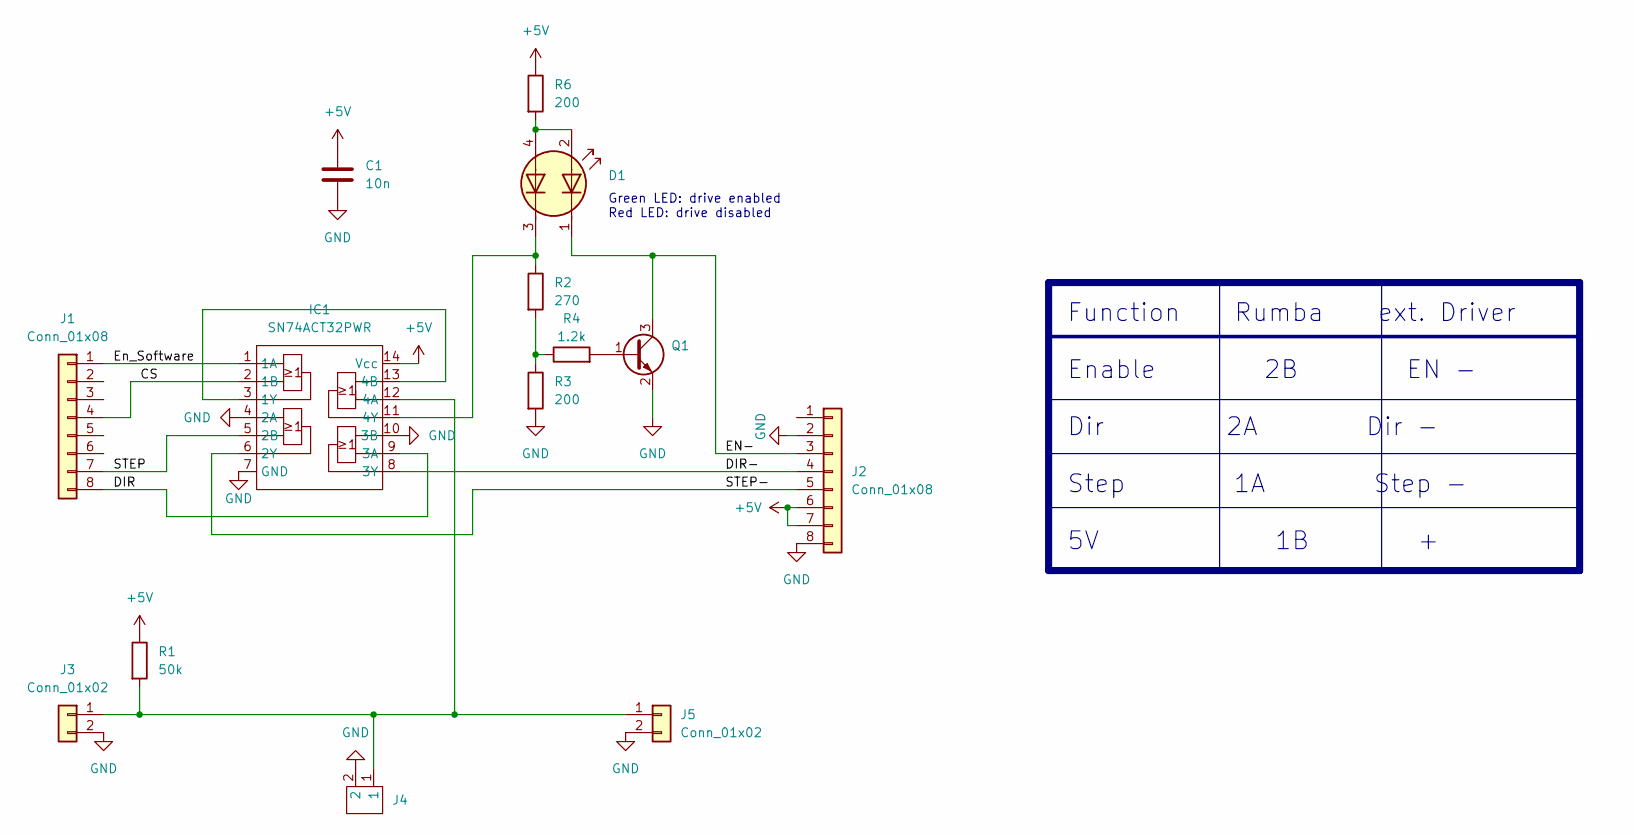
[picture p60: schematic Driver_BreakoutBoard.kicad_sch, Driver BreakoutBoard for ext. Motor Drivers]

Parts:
C1: 10n; C_0805_2012Metric_Pad1.18x1.45mm_HandSolder
D1: LED_Dual; LED_Kingbright_AAA3528ESGCT
IC1: SN74ACT32PWR; SOT402-1_NXP-M
J1, J2: Conn_01x08; PinHeader_1x08_P2.54mm_Vertical
J3, J5: Conn_01x02; PinHeader_1x02_P2.54mm_Vertical
J4: 0393570002
Q1: Q_NPN_CEB; SOT-23_Handsoldering
R1: 50k; R_0805_2012Metric_Pad1.20x1.40mm_HandSolder
R2: 270; R_0805_2012Metric_Pad1.20x1.40mm_HandSolder
R3, R6: 200; R_0805_2012Metric_Pad1.20x1.40mm_HandSolder
R4: 1.2k; R_0805_2012Metric_Pad1.20x1.40mm_HandSolder

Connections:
+5V: C1.1, IC1.14 (Vcc), J2.6, J2.7, R1.1, R6.1
/CS: IC1.2 (1B), J1.4
/DIR: IC1.9 (3A), J1.8
/DIR-: IC1.8 (3Y), J2.4
/EN-: D1.1 (A1), J2.3, Q1.3 (C)
/En_Software: IC1.1 (1A), J1.1
/STEP: IC1.5 (2B), J1.7
/STEP-: IC1.6 (2Y), J2.5
GND: C1.2, IC1.4 (2A), IC1.7 (GND), IC1.10 (3B), J2.2, J2.8, J3.2, J4.2, J5.2, Q1.2 (E), R3.2
unnamed: D1.2 (K1), D1.4 (K2), R6.2
unnamed: D1.3 (A2), IC1.11 (4Y), R2.1
unnamed: IC1.12 (4A), J3.1, J4.1, J5.1, R1.2
unnamed: IC1.3 (1Y), IC1.13 (4B)
unnamed: Q1.1 (B), R4.2
unnamed: R2.2, R3.1, R4.1

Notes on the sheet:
Function Rumba ext. Driver Enable 2B EN - Dir 2A Dir - Step 1A Step - 5V 1B +
Green LED: drive enabled Red LED: drive disabled

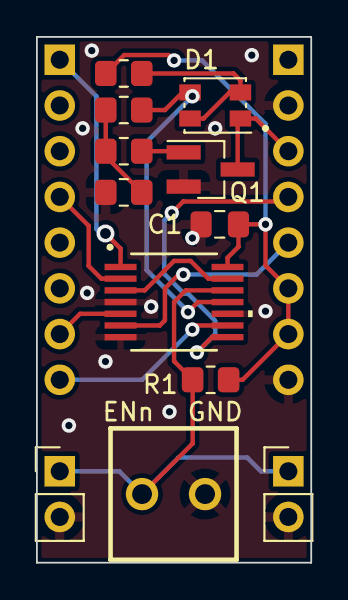
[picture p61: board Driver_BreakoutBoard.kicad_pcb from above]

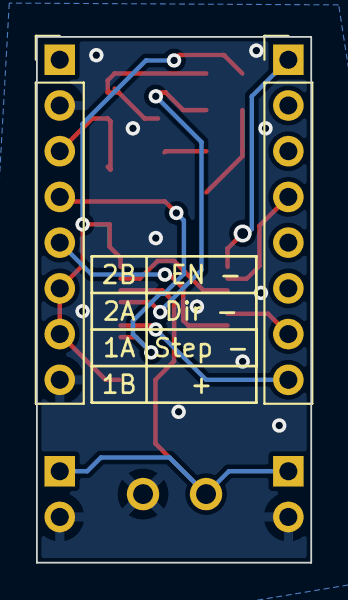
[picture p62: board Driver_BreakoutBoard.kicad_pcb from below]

Board: 2 copper layers, 15.2 x 29.2 mm, 14 parts (2 on the bottom side), 15 nets.

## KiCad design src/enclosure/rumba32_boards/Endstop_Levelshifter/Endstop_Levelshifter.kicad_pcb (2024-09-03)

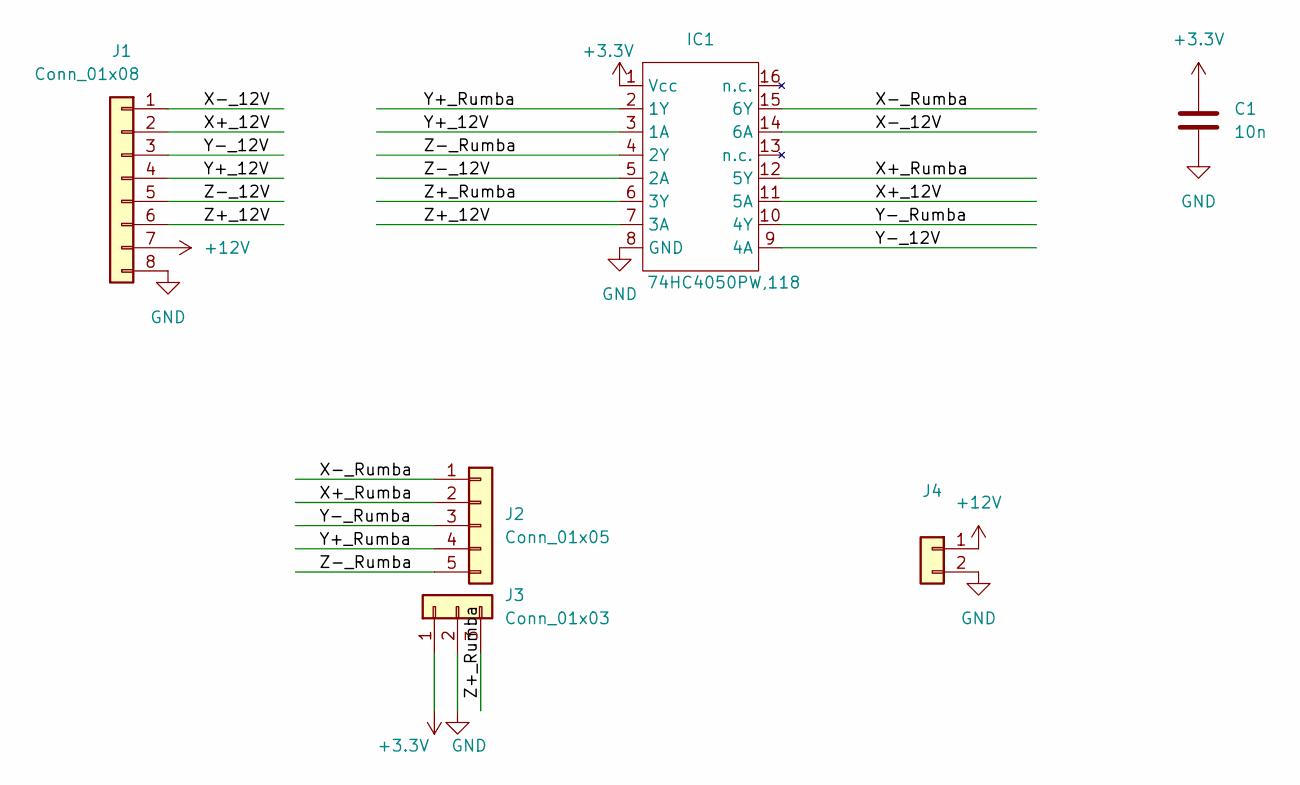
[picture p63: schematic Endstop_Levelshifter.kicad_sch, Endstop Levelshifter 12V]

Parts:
C1: 10n; C_0805_2012Metric_Pad1.18x1.45mm_HandSolder
IC1: 74HC4050PW,118; TSSOP-16_4.4x5mm_P0.65mm
J1: Conn_01x08; 691210910008
J2: Conn_01x05; PinSocket_1x05_P2.54mm_Vertical
J3: Conn_01x03; PinSocket_1x03_P2.54mm_Vertical
J4: Conn_01x02; PinHeader_1x02_P2.54mm_Horizontal

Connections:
+3.3V: C1.1, IC1.1 (Vcc), J3.1
+12V: J1.7, J4.1
/X+_12V: IC1.11 (5A), J1.2
/X+_Rumba: IC1.12 (5Y), J2.2
/X-_12V: IC1.14 (6A), J1.1
/X-_Rumba: IC1.15 (6Y), J2.1
/Y+_12V: IC1.3 (1A), J1.4
/Y+_Rumba: IC1.2 (1Y), J2.4
/Y-_12V: IC1.9 (4A), J1.3
/Y-_Rumba: IC1.10 (4Y), J2.3
/Z+_12V: IC1.7 (3A), J1.6
/Z+_Rumba: IC1.6 (3Y), J3.3
/Z-_12V: IC1.5 (2A), J1.5
/Z-_Rumba: IC1.4 (2Y), J2.5
GND: C1.2, IC1.8 (GND), J1.8, J3.2, J4.2

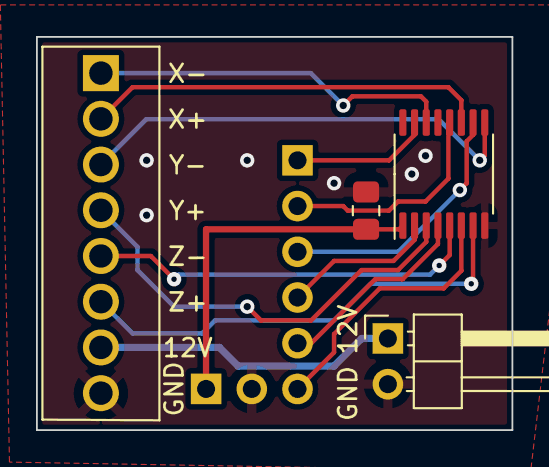
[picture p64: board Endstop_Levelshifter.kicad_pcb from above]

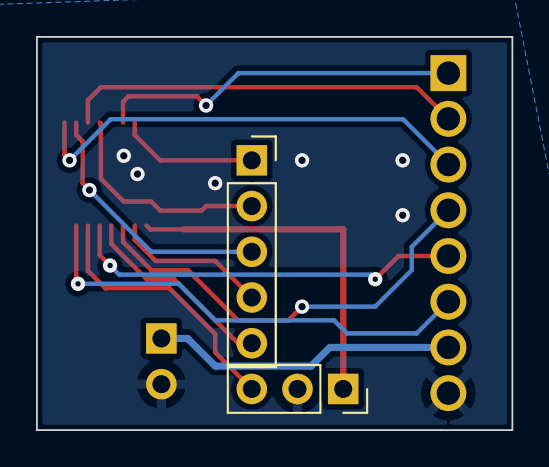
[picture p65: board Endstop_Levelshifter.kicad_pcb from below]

Board: 2 copper layers, 26.4 x 21.8 mm, 6 parts (2 on the bottom side), 15 nets.

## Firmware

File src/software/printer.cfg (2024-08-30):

# This file contains common pin mappings for MKS RUMBA32 boards.  To use
# this config, the firmware should be compiled for the STMicroelectronics STM32,
# Processor model STM32F446, Clock Reference 12 MHz crystal.

# See docs/Config_Reference.md for a description of parameters.

[mcu]
#serial: 1d50:614e 
# The line below needs to be changed for your specific board - you can get the correct value via ls /dev/serial/by-id/*
serial: /dev/serial/by-id/usb-Klipper_stm32f446xx_12345-if00
#serial: /dev/serial0
#   The serial port to connect to the MCU. If unsure (or if it
#   changes) see the "Where's my serial port?" section of the FAQ.
#   This parameter must be provided when using a serial port.
baud: 250000
#   The baud rate to use. The default is 250000.
#canbus_uuid:
#   If using a device connected to a CAN bus then this sets the unique
#   chip identifier to connect to. This value must be provided when using
#   CAN bus for communication.
#canbus_interface:
#   If using a device connected to a CAN bus then this sets the CAN
#   network interface to use. The default is 'can0'.
restart_method: command
#   This controls the mechanism the host will use to reset the
#   micro-controller. The choices are 'arduino', 'cheetah', 'rpi_usb',
#   and 'command'. The 'arduino' method (toggle DTR) is common on
#   Arduino boards and clones. The 'cheetah' method is a special
#   method needed for some Fysetc Cheetah boards. The 'rpi_usb' method
#   is useful on Raspberry Pi boards with micro-controllers powered
#   over USB - it briefly disables power to all USB ports to
#   accomplish a micro-controller reset. The 'command' method involves
#   sending a Klipper command to the micro-controller so that it can
#   reset itself. The default is 'arduino' if the micro-controller
#   communicates over a serial port, 'command' otherwise.

[printer]
kinematics: cartesian
#   The type of printer in use. This option may be one of: cartesian,
#   corexy, corexz, hybrid_corexy, hybrid_corexz, rotary_delta, delta,
#   deltesian, polar, winch, or none. This parameter must be specified.
max_velocity: 50
#   Maximum velocity (in mm/s) of the toolhead (relative to the
#   print). This parameter must be specified.
max_accel: 20
#   Maximum acceleration (in mm/s^2) of the toolhead (relative to the
#   print). This parameter must be specified.
#max_accel_to_decel:
#   A pseudo acceleration (in mm/s^2) controlling how fast the
#   toolhead may go from acceleration to deceleration. It is used to
#   reduce the top speed of short zig-zag moves (and thus reduce
#   printer vibration from these moves). The default is half of
#   max_accel.
#square_corner_velocity: 5.0
#   The maximum velocity (in mm/s) that the toolhead may travel a 90
#   degree corner at. A non-zero value can reduce changes in extruder
#   flow rates by enabling instantaneous velocity changes of the
#   toolhead during cornering. This value configures the internal
#   centripetal velocity cornering algorithm; corners with angles
#   larger than 90 degrees will have a higher cornering velocity while
#   corners with angles less than 90 degrees will have a lower
#   cornering velocity. If this is set to zero then the toolhead will
#   decelerate to zero at each corner. The default is 5mm/s.

#[output_pin !X_Enable]
#pin:!PC11
#   The pin to configure as an output. This parameter must be
#   provided.
#pwm: False

#   Set if the output pin should be capable of pulse-width-modulation.
#   If this is true, the value fields should be between 0 and 1; if it
#   is false the value fields should be either 0 or 1. The default is
#   False.
#static_value:
#   If this is set, then the pin is assigned to this value at startup
#   and the pin can not be changed during runtime. A static pin uses
#   slightly less ram in the micro-controller. The default is to use
#   runtime configuration of pins.
#value:1
#   The value to initially set the pin to during MCU configuration.
#   The default is 0 (for low voltage).

[stepper_x]
step_pin: PA0
#   Step GPIO pin (triggered high). This parameter must be provided.
dir_pin: !PC15
#   Direction GPIO pin (high indicates positive direction). This
#   parameter must be provided.
enable_pin: !PC11
#   Enable pin (default is enable high; use ! to indicate enable
#   low). If this parameter is not provided then the stepper motor
#   driver must always be enabled.
rotation_distance: 5
#   Distance (in mm) that the axis travels with one full rotation of
#   the stepper motor (or final gear if gear_ratio is specified).
#   This parameter must be provided.
microsteps: 64 #128
#   The number of microsteps the stepper motor driver uses. This
#   parameter must be provided.
full_steps_per_rotation: 200
#   The number of full steps for one rotation of the stepper motor.
#   Set this to 200 for a 1.8 degree stepper motor or set to 400 for a
#   0.9 degree motor. The default is 200.
#gear_ratio:
#   The gear ratio if the stepper motor is connected to the axis via a
#   gearbox. For example, one may specify "5:1" if a 5 to 1 gearbox is
#   in use. If the axis has multiple gearboxes one may specify a comma
#   separated list of gear ratios (for example, "57:11, 2:1"). If a
#   gear_ratio is specified then rotation_distance specifies the
#   distance the axis travels for one full rotation of the final gear.
#   The default is to not use a gear ratio.
step_pulse_duration: 0.0000035 # 3,5 µs
#   The minimum time between the step pulse signal edge and the
#   following "unstep" signal edge. This is also used to set the
#   minimum time between a step pulse and a direction change signal.
#   The default is 0.000000100 (100ns) for TMC steppers that are
#   configured in UART or SPI mode, and the default is 0.000002 (which
#   is 2us) for all other steppers.
endstop_pin: !PB12
#   Endstop switch detection pin. If this endstop pin is on a
#   different mcu than the stepper motor then it enables "multi-mcu
#   homing". This parameter must be provided for the X, Y, and Z
#   steppers on cartesian style printers.
#position_min: 0
#   Minimum valid distance (in mm) the user may command the stepper to
#   move to.  The default is 0mm.
position_endstop: 0
#   Location of the endstop (in mm). This parameter must be provided
#   for the X, Y, and Z steppers on cartesian style printers.
position_max: 497
#   Maximum valid distance (in mm) the user may command the stepper to
#   move to. This parameter must be provided for the X, Y, and Z
#   steppers on cartesian style printers.
homing_speed: 20
#   Maximum velocity (in mm/s) of the stepper when homing. The default
#   is 5mm/s.
homing_retract_dist: 5
#   Distance to backoff (in mm) before homing a second time during
#   homing. Set this to zero to disable the second home. The default
#   is 5mm.
homing_retract_speed: 5
#   Speed to use on the retract move after homing in case this should
#   be different from the homing speed, which is the default for this
#   parameter
#second_homing_speed:
#   Velocity (in mm/s) of the stepper when performing the second home.
#   The default is homing_speed/2.
homing_positive_dir: false
#   If true, homing will cause the stepper to move in a positive
#   direction (away from zero); if false, home towards zero. It is
#   better to use the default than to specify this parameter. The
#   default is true if position_endstop is near position_max and false
#   if near position_min.
##gear_ratio:
#   The gear ratio if the stepper motor is connected to the axis via a
#   gearbox. For example, one may specify "5:1" if a 5 to 1 gearbox is
#   in use. If the axis has multiple gearboxes one may specify a comma
#   separated list of gear ratios (for example, "57:11, 2:1"). If a
#   gear_ratio is specified then rotation_distance specifies the
#   distance the axis travels for one full rotation of the final gear.
#   The default is to not use a gear ratio.


[stepper_y]
step_pin: PE5
dir_pin: PE6
enable_pin: !PE3
microsteps: 64
rotation_distance: 5
step_pulse_duration: 0.0000035 # 3,5 µs
endstop_pin: !PB15
position_endstop: 0
position_max: 460
homing_speed: 20
homing_retract_dist: 5
homing_retract_speed: 5
homing_positive_dir: false


[stepper_z]
step_pin: PE1
dir_pin: !PE2
enable_pin: !PB7
microsteps: 64
rotation_distance: 5
step_pulse_duration: 0.0000035 # 3,5 µs
endstop_pin: !PD9
position_endstop: 0.5
position_max: 610
homing_speed: 20
homing_retract_dist: 5
homing_retract_speed: 5
homing_positive_dir: false


[extruder]
step_pin: PB5
dir_pin: PB6
enable_pin: !PC12
microsteps: 16
rotation_distance: 33.500
nozzle_diameter: 0.400
filament_diameter: 1.750
heater_pin: PC6
sensor_type: NTC 100K MGB18-104F39050L32
sensor_pin: PC4
control: pid
pid_Kp: 22.2
pid_Ki: 1.08
pid_Kd: 114
min_temp: 0
max_temp: 2500

#[extruder1]
#step_pin: PD6
#dir_pin: PD7
#enable_pin: !PD4
#heater_pin: PC7
#sensor_pin: PC3
#...

#[extruder2]
#step_pin: PD2
#dir_pin: PD3
#enable_pin: !PD0
#heater_pin: PC8
#sensor_pin: PC2
#...

[heater_bed]
heater_pin: PA1
sensor_type: NTC 100K MGB18-104F39050L32
sensor_pin: PC0
control: watermark
min_temp: 0
max_temp: 130

[fan]
pin: PC9

#[heater_fan fan1]
#pin: PA8

# Kill-Switch
[gcode_button kill_switch]
pin: PC5
press_gcode: M112



[printer]
kinematics: cartesian
max_velocity: 300#300
max_accel: 20#3000
max_z_velocity: 200
max_z_accel: 20


########################################
# EXP1 / EXP2 (display) pins
########################################

[board_pins]
aliases:
    # EXP1 header
    EXP1_1=PE8, EXP1_3=PE9, EXP1_5=PE12, EXP1_7=PE14, EXP1_9=<GND>,
    EXP1_2=PE7, EXP1_4=PE10, EXP1_6=PE13, EXP1_8=PE15, EXP1_10=<5V>,
    # EXP2 header
    EXP2_1=PA6, EXP2_3=PB2, EXP2_5=PB1, EXP2_7=PB0,  EXP2_9=<GND>,
    EXP2_2=PA5, EXP2_4=PA2, EXP2_6=PA7, EXP2_8=<RST>, EXP2_10=PC5,


[output_pin X_CS]
pin: PC14

[output_pin Y_CS]
pin: PE4

[output_pin Z_CS]
pin: PE0

[output_pin E0_CS]
pin: PC13

[output_pin E1_CS]
pin: PD5

[output_pin E2_CS]
pin: PD1


[gcode_macro hard_disable_drives]
description: Disables all motors. Software realizes nothing from it.
gcode:
  G4 P125
  SET_PIN PIN=X_CS VALUE=1
  SET_PIN PIN=Y_CS VALUE=1
  SET_PIN PIN=Z_CS VALUE=1
  SET_PIN PIN=E0_CS VALUE=1
  SET_PIN PIN=E1_CS VALUE=1
  SET_PIN PIN=E2_CS VALUE=1
  G4 P125


[gcode_macro hard_enable_drives]
description: Disables all motors. Software realizes nothing from it.
gcode:
  G4 P125
  SET_PIN PIN=X_CS VALUE=0
  SET_PIN PIN=Y_CS VALUE=0
  SET_PIN PIN=Z_CS VALUE=0
  SET_PIN PIN=E0_CS VALUE=0
  SET_PIN PIN=E1_CS VALUE=0
  SET_PIN PIN=E2_CS VALUE=0
  G4 P125


[gcode_arcs] #enables G2 and G3


# See the sample-lcd.cfg file for definitions of common LCD displays.


########################################
# TMC2209 configuration
########################################

#[tmc2209 stepper_x]
#uart_pin: PC14
##tx_pin: PA3
#run_current: 0.800
#diag_pin:

#[tmc2209 stepper_y]
#uart_pin: PE4
##tx_pin: PA4
#run_current: 0.800
#diag_pin:

#[tmc2209 stepper_z]
#uart_pin: PE0
##tx_pin: PD13
#run_current: 0.800
#diag_pin:

#[tmc2209 extruder]
#uart_pin: PC13
##tx_pin: PD14
#run_current: 0.600
#diag_pin:

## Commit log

2024-07-12 Fixed link for pe cage clamp.
    [bom-electronic-cabinet.csv]
2024-07-29 Fixed mistakes in X1 wiring table.
2024-07-29 Updated PowerSupply schematic.
2024-08-29 Updated with new PCB Layout.
    [Driver_BreakoutBoard.kicad_pcb, Driver_BreakoutBoard.kicad_sch]
2024-08-29 Small improvement to board layout.
    [Driver_BreakoutBoard.kicad_pcb]
2024-09-02 Updated electrical BoM.
    [bom-electronic-cabinet.csv]
2024-09-02 Updated electrical assembly instructions.
    [complete_system.skp]
2024-09-03 Removed old assembly instructions.
    [2018-08-24_cosi-measure_v1.0_BoM_mechanical.ods]
2024-09-03 Updated directory structure.
    [Driver_BreakoutBoard.kicad_pcb, Driver_BreakoutBoard.kicad_sch, Endstop_Levelshifter-B_Cu.gbl, Endstop_Levelshifter-B_Mask.gbs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]
